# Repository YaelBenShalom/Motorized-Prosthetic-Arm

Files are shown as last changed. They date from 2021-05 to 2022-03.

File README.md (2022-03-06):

# The Design and Control of a Motorized Prosthetic Arm

Author: Yael Ben Shalom<br>
Final project, MS in Robotics at Northwestern, 2021.

## Table of Contents

- [Project Description](#project-description)
- [Project Overview](#project-overview)
- [Getting Started](#getting-started)

## Project Description

In this project, I designed, built, and controlled a motorized prosthetic elbow that imitates healthy arm motion to help amputees prevent falling, avoid injuries, and maintain balance while walking. According to [Kent and Major's research](https://www.sciencedirect.com/science/article/abs/pii/S0268003320301248?casa_token=pASJip1O0HgAAAAA:ckojZ8F55NSTF2rAq7aVUub568BDZgnYYnto9notnVSgfjbTsNp5ktE2Q-ZMWgL62Lgc80yd), asymmetries in body mass and motion affect the regulation of whole-body angular momentum in individuals with upper limb absence and may increase fall risk.

To better predict the arm-body motion, I analyzed arm movement data patterns, simulated full arm dynamics, and found the relation between walking speed to the angular velocity of the arm.

Please visit [my website](https://yaelbenshalom.github.io/motorized_prosthetic_arm/index.html) for more information about this project.

## Project Overview

This project contains 4 parts:

1. [Data collection](https://github.com/YaelBenShalom/Motorized-Prosthetic-Arm/tree/master/data)
2. [Arm motion analysis and modeling](https://github.com/YaelBenShalom/Motorized-Prosthetic-Arm/tree/master/motor_control/arm_pendulum_modeling)
3. [Motor control to achieve the desired arm motion](https://github.com/YaelBenShalom/Motorized-Prosthetic-Arm/tree/master/motor_control)
4. [Mechanical design of the prosthetic elbow](https://github.com/YaelBenShalom/Motorized-Prosthetic-Arm/tree/master/mech_design)

## Getting Started

1. Clone the repository:
    ```
    git clone https://github.com/YaelBenShalom/Motorized-Prosthetic-Arm.git
    ```

2. Install the `odrive-tool` package. For installation instructions, visit the [ODrive getting-started page](https://docs.odriverobotics.com/).

3. Assemble the system according to the system sketch.

4. Connect the module to the computer's USB port and upload the desired ODrive configuration by running:
    ```
    python3 setup.py
    ```

    The controller might need an additional tunning. Follow the tunning instructions on the [ODrive control page](https://docs.odriverobotics.com/control).

5. Activate the system by running:
    ```
    python3 motor_control/odrive_control.py --velocity=<walking velocity>
    ```

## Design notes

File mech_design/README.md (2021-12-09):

# The Design and Control of a Motorized Prosthetic Arm

Author: Yael Ben Shalom<br>
Final project, MS in Robotics at Northwestern, 2021.

## Mechanical Design of the Prosthetic Elbow

The system contained several key parts:

1. Motor (T-Motor, R60 KV115)
2. Encoder PCB (Designed for a Magnetic Rotary Encoder (AS5048A))
3. Driver (ODrive V3.6, 24V)
4. Odrive Adaptor PCB (Adaptor from ODrive connector to ethernet connector)
5. Elbow packaging (based on [Fillauer E-400](https://www.spsco.com/hosmer-e-400.html))
6. Battery

<p align="center">
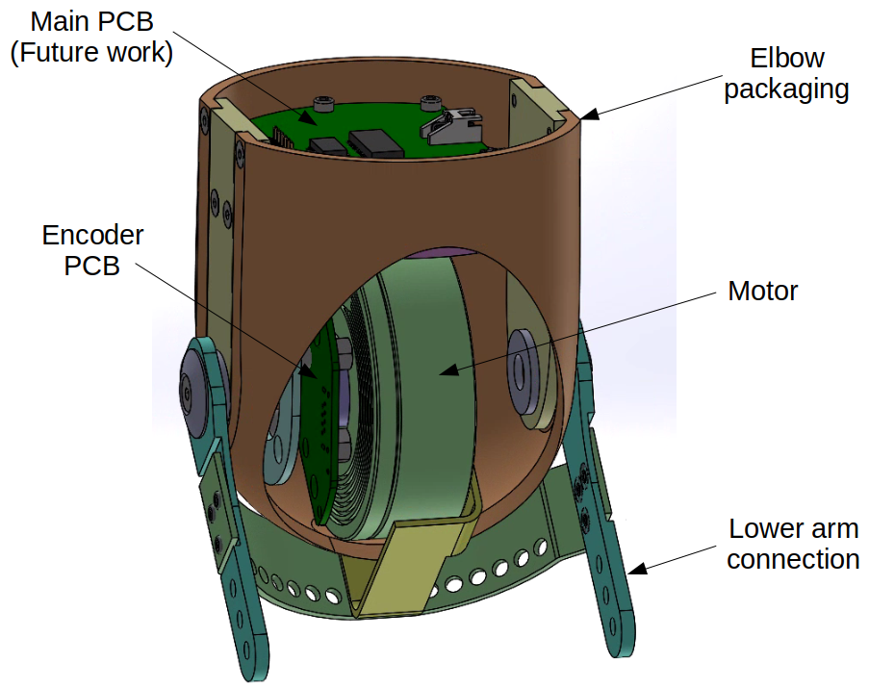
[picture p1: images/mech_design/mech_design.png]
  
</p>

All 3D CAD files can be found [here](https://github.com/YaelBenShalom/Motorized-Prosthetic-Arm/tree/master/mech_design), and all circuit board schematics and manufacture files can be found [here](https://github.com/YaelBenShalom/Motorized-Prosthetic-Arm/tree/master/board_design).

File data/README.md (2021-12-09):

# The Design and Control of a Motorized Prosthetic Arm

Author: Yael Ben Shalom<br>
Final project, MS in Robotics at Northwestern, 2021.

## Data Collection

In this part of the project, I focused on measuring prosthetics characteristics and collecting body-arm motion data.<br>
For further information about data collection please visit [my website](https://yaelbenshalom.github.io/motorized_prosthetic_arm/index.html).

This section contains all the data collected in this project and the scripts used to process it. It contains 2 main parts:
1. Prosthetic Measurements (length, mass, and center of mass location) to define the average prosthetic the device should support.
2. Walking data was collected from people with and without upper limb absence (including myself). The data was collected using sensors attached to the body in various locations (forearm, upper arm, lower back, etc.), that measured the body's angles, velocities, and accelerations. these were later used to explore the body-arm dynamics while walking, and to find the correlation between walking speed and arm swing

An example of the outputs of the sensors are presented in the following video:

<p align="center">
  
</p>

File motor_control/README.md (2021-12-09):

# The Design and Control of a Motorized Prosthetic Arm

Author: Yael Ben Shalom<br>
Final project, MS in Robotics at Northwestern, 2021.

## Motor Control to Achieve the Desired Arm Motion

To control the motor, I used a 2 layer control system - feedback current and position control. The current was controlled by the ODrive's controller, and the position was controlled by a feedback PID controller (with an optional feedforward component).

The control system diagram:

<p align="center">
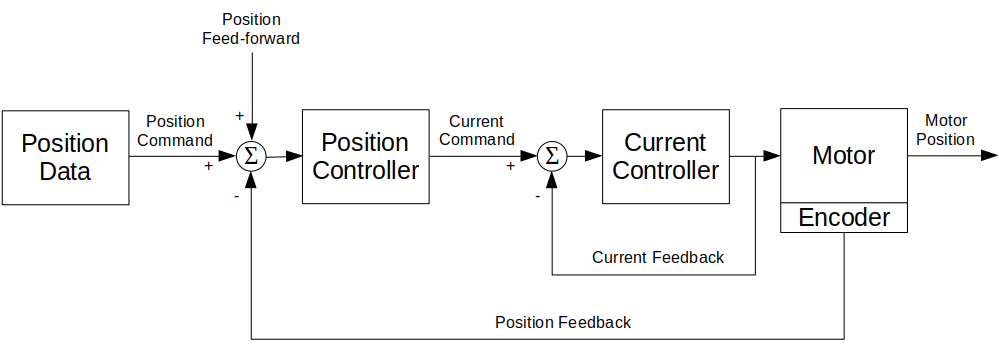
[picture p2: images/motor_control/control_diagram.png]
  
</p>

The PID position control diagram:

<p align="center">
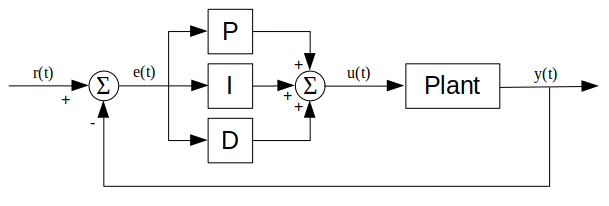
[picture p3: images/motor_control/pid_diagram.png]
  
</p>

An example of motor position control using the PID controller. The blue plot is the input angles, the red plot is the controlled output angles, and the second graph is the error changing with time:

<p align="center">
  
</p>

<p align="center">
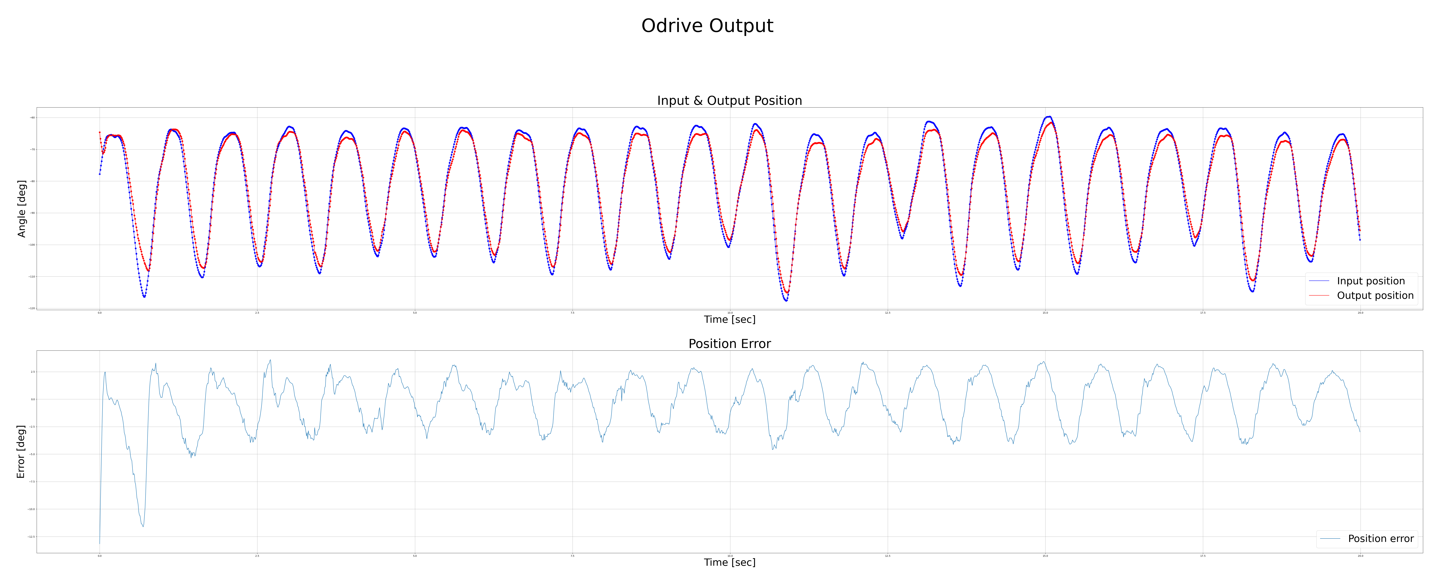
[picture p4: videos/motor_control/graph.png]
  
</p>

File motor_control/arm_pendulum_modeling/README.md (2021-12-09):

# The Design and Control of a Motorized Prosthetic Arm

Author: Yael Ben Shalom<br>
Final project, MS in Robotics at Northwestern, 2021.

## Arm Motion Analysis and Modeling

To Better understand the motion of a human arm and find a suitable motor to imitate the elbow motion, I modeled the arm as a double pendulum system. I used the system Lagrangian and measured shoulder and elbow angles to find the motion equations and extract the required elbow torque. More explanations about the theoretical aspects of the method and calculations can be found [here](https://yaelbenshalom.github.io/motorized_prosthetic_arm/index.html).

The double pendulum can be described using the following system sketch, where the masses are located in the center of mass of every link:

<p align="center">
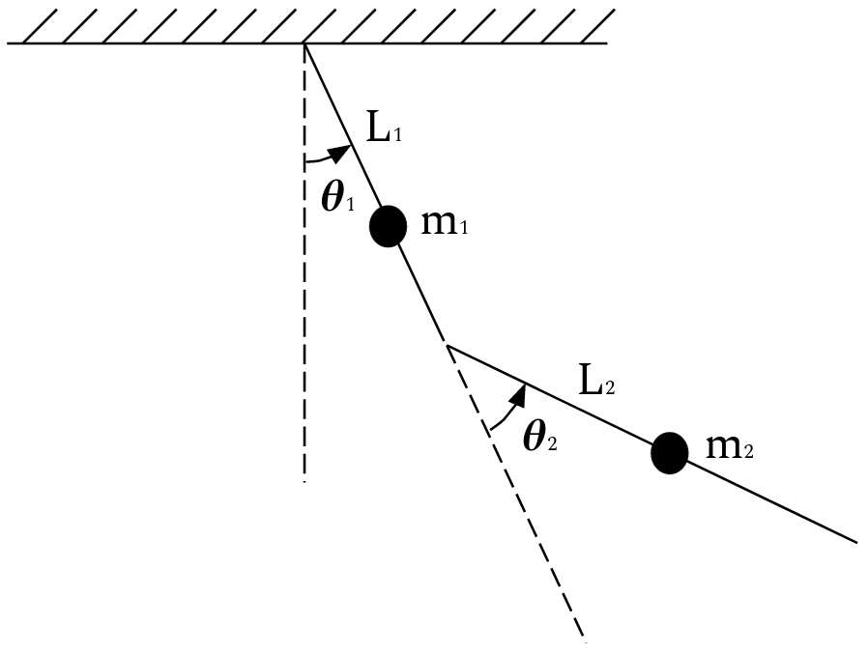
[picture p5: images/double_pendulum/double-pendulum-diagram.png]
  
</p>

The following video shows an animation of the arm motion, represented as a double pendulum:

<p align="center">
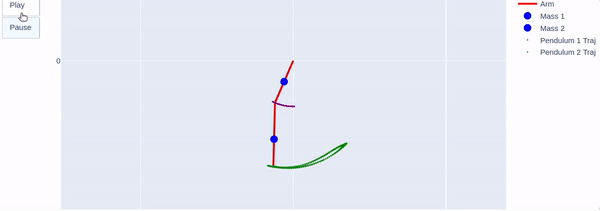
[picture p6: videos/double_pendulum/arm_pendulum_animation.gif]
  
</p>

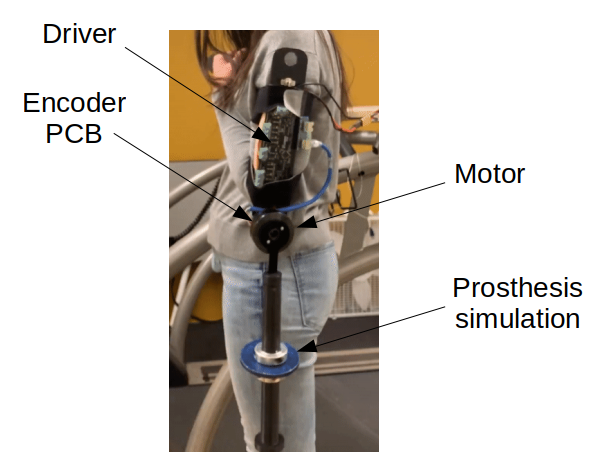
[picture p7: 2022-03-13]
images/mech_design/Prototype.png

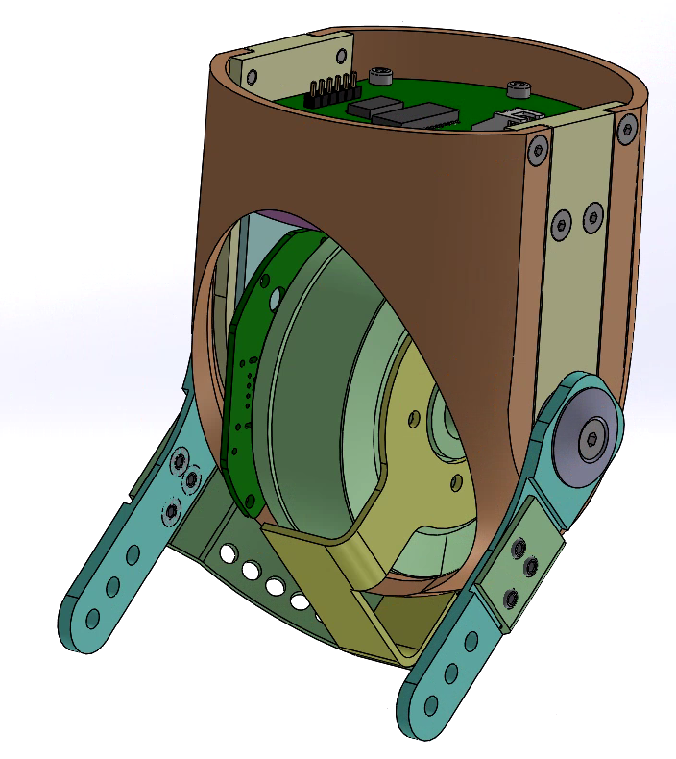
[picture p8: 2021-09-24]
images/mech_design/mech_design3.png

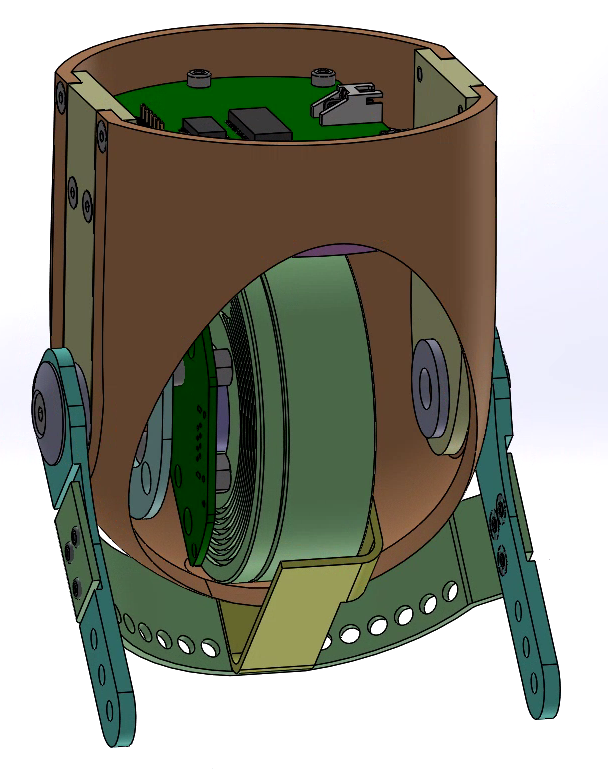
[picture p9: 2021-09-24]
images/mech_design/mech_design2.png

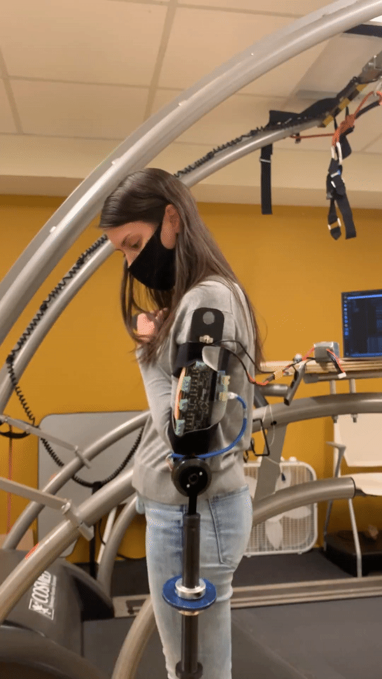
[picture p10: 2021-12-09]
images/mech_design/prototype2.png

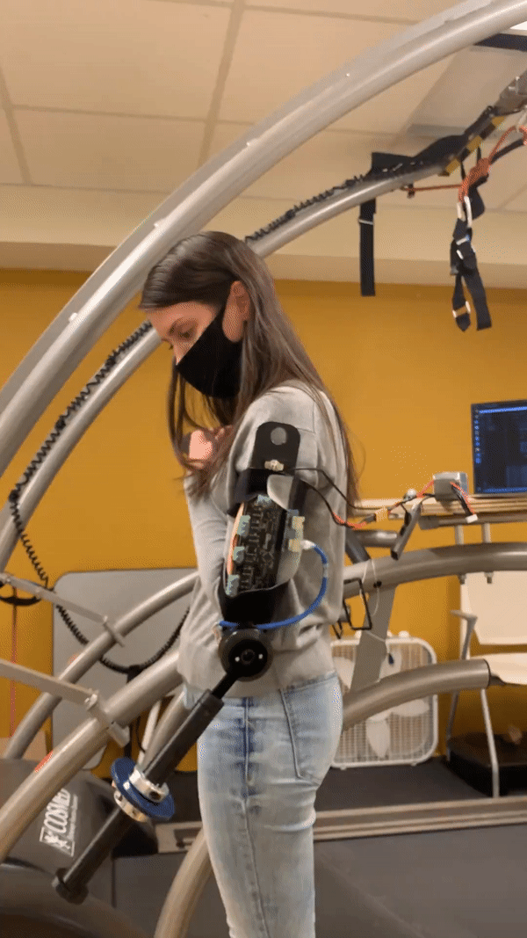
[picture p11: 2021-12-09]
images/mech_design/prototype1.png

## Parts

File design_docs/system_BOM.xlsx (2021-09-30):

Module | Component | Quantity | Purpose | Source
PCB | MPLAB Snap | 1 | Program the PIC | https://www.digikey.com/en/products/detail/PG164100/PG164100-ND/9562532?itemSeq=359206540
 | PIC32MX170F256B-50I/SP | 1 | PIC32 microcontroller - bread board | https://www.digikey.com/en/products/detail/microchip-technology/PIC32MX170F256B-50I-SS/4902613
 | PIC32MX170F256B-50I/SO | 1 | PIC32 microcontroller - PCB | https://www.digikey.com/en/products/detail/microchip-technology/PIC32MX170F256B-50I-SO/4902611
 | micro USB cable | 3 | power, programming and communication | https://www.digikey.com/en/products/detail/3025010-03/Q853-ND/4341883?itemSeq=359206541
 | 8 MHz resonator | 1 | PIC clock source | https://www.digikey.com/en/products/detail/CSTLS8M00G53-B0/490-1212-ND/584420?itemSeq=359206536
 | Pushbutton | 3 | Reset and User buttons | https://www.digikey.com/en/products/detail/EVQ-11A07K/P8072SCT-ND/259557?itemSeq=359206539
 | Green LED | 3 | indication | https://www.digikey.com/en/products/detail/WP132XGD/754-1210-ND/1747609?itemSeq=359206537
 | Red LED | 3 | indication | https://www.digikey.com/en/products/detail/WP132XID/754-1211-ND/1747610?itemSeq=359206531
 | Yellow LED | 3 | indication | https://www.digikey.com/en/products/detail/WP132XYD/754-1212-ND/1747611?itemSeq=359206534
 | 0.1uF capacitor | 5 | bypass | https://www.digikey.com/en/products/detail/K104Z15Y5VE5TL2/BC1148TR-ND/286602
 | 10uF tantalum capacitor | 1 | prototyping
 | 330 ohm resistor | 10 | LED current limit | https://www.digikey.com/en/products/detail/CF14JT330R/CF14JT330RTR-ND/1741399
 | 10k ohm resistor | 10 | pull-up | https://www.digikey.com/en/products/detail/CF14JT10K0/CF14JT10K0TR-ND/1741265
 | Slide switch | 1 | power on/off | https://www.adafruit.com/product/805
 | 6 DOF IMU | 1 | motion sensing | https://www.adafruit.com/product/4480
 | CP2104 Friend | 1 | USB to UART | https://www.adafruit.com/product/3309
 | micro USB connector breakout | 1 | breadboard power | https://www.pololu.com/product/2586
 | DRV8835 breakout board | 1 | dual H-bridge | https://www.pololu.com/product/2135
 | 3.3V step up / step down | 1 | voltage regulator | https://www.pololu.com/product/2122
 | Extra long header pins | 6+3 | prototyping | https://www.aliexpress.com/item/32651418137.html?spm=a2g0s.9042311.0.0.50904c4dIFFWhE
 | micro USB connector | 1 | PCB | https://www.digikey.com/en/products/detail/amphenol-icc-fci/10118194-0001LF/2785389
 | 28 position socket | 1 | PCB | https://www.digikey.com/en/products/detail/on-shore-technology-inc/ED281DT/4147600
Motor | R60 KV115 | 1 | Motor | https://store.tmotor.com/goods.php?id=943
Encoder | AS5048A-HTSP-500 | 1 | Encoder | https://www.digikey.com/en/products/detail/ams/AS5048A-HTSP-500/3188615
Driver | ODRIVE V3.6 | 1 | Driver | https://odriverobotics.com/shop/odrive-v36
Battery
Prototype | Breadboard | 3 | prototyping | https://www.circuitspecialists.com/solderless-breadboard-wb-102.html
 | Wire | 6 | prototyping | https://www.amazon.com/Tnisesm-Breadboard-Tweezers-Prototyping-Circuits/dp/B096K4SYTX
 | Bettomshin 2Pcs AXK0619 Thrust Needle Roller Bearings 0.24" x 0.75" x 0.16" High Carbon Chromium Bearing Steel Thrust Rolling Bearings with Washers | 2 | thrust bearing | https://www.amazon.com/dp/B08Z47TLR3 (https://www.amazon.com/dp/B08Z47TLR3?spLa=ZW5jcnlwdGVkUXVhbGlmaWVyP)
 | Bettomshin 2Pcs AXK0821 Thrust Needle Roller Bearings 0.31" x 0.83" x 0.08" High Carbon Chromium Bearing Steel Thrust Rolling Bearings with Washers | 2 | thrust bearing | https://www.amazon.com/dp/B08Z47FC6W (https://www.amazon.com/dp/B08Z47FC6W?spLa=ZW5jcnlwdGVkUXVhbGlmaWVyP)
 | 32 Mbit flash | 1 | memory for audio project | https://www.digikey.com/en/products/detail/W25Q32JVDAIQ/W25Q32JVDAIQ-ND/5803977?itemSeq=359206549
 | MCP23017 | 1 | I2C IO expander | https://www.digikey.com/en/products/detail/MCP23017-E%2fSP/MCP23017-E%2fSP-ND/894272?itemSeq=359206544
 | MCP4912 | 1 | SPI DAC | https://www.digikey.com/en/products/detail/MCP4912-E%2fP/MCP4912-E%2fP-ND/2332828?itemSeq=359206545
 | WS2812B | 5 | Addressable RGB LED (Neopixel) | https://www.digikey.com/en/products/detail/COM-12877/1568-1202-ND/5673788?itemSeq=359206543
 | L4931 3.3V regulator | 1

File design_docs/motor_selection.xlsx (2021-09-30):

 |  | Format legend: | Row checked by Bill | inferred/calculated spec |  | vendor spec | ~ = unknown | guess based on similar product
 |  |  |  |  |  |  |  |  |  |  |  |  |  |  |  |  |  |  |  |  |  |  | Normalized (1-normal for undesirable)
Vendor | Name | Rated Voltage (V) | Rated Current (A) | Peak Current (A) | Power (W) | Stall Current (A) | Rwinding (Ω) | Rated τ (Nm) | Peak τ (Nm) | Stall τ (Nm) | Rated ω (rpm) | Free ω (rpm) | Kv (rpm/V) | Reduction | MOI (g*cm²) | Pole Pairs | Mass (g) | Price | Stall τ to weight (Nm/kg) | Stall loss (W) | Effective Km | Notes | Stall τ to weight (Nm/kg) | Stall loss (W) | Effective Km | Average normal metric |  | Stall Diff (A) | Stall Diff Power (W)
T-Motor | G35 (https://uav-en.tmotor.com/html/2021/G_0106/653.html) | 16 | 1.45 | 4.5 | 23.2 | 4.5 | 3.33 | 0.15 | 0.46 | 0.46 | 900 | 1500 | 100 | 1 | 61 | 7 | 159 | $54.99 | 2.893081761 | 72 | 0.05421151989 |  | #DIV/0! | 0.99265625 | 0.03901156848 | #DIV/0! |  | 0.3048048048 | 4.876876877
T-Motor | AK80-6 (http://store-new.tmotor.com/goods.php?id=981) | 24 | 12 | 24 | 288 | 141.1764706 | 0.17 | 6 | 12 | 80.88815931 | 365 | 460 | 100 | 6 | ~ | 21 | 485 | $569.90 | 166.7797099 | 3388.235294 | 1.38962677 | Gearbox | #DIV/0! | 0.6544117647 | 1 |  | <-omitted from color scale | 0 | 0
T-Motor | G40 (https://uav-en.tmotor.com/html/2021/G_0106/652.html) | 16 | 1.65 | 5 | 26.4 | 5 | 3.6 | 0.25 | 0.73 | 0.73 | 600 | 1050 | 70 | 1 | 74 | 14 | 183 | $72.99 | 3.989071038 | 80 | 0.08161648118 |  | #DIV/0! | 0.9918402778 | 0.0587326633 | #DIV/0! |  | -0.5555555556 | -8.888888889
T-Motor | G60 (https://uav-en.tmotor.com/html/2021/G_0106/651.html) | 24 | 1.43 | 4.2 | 34.32 | 4.2 | 4.6 | 0.6 | 1.75 | 1.75 | 350 | 560 | 25 | 1 | 355 | 14 | 374 | $108.99 | 4.679144385 | 100.8 | 0.1743041722 |  | #DIV/0! | 0.98971875 | 0.125432365 | #DIV/0! |  | 1.017391304 | 24.4173913
ODrive | D5065 270KV (https://odriverobotics.com/shop/odrive-custom-motor-d5065) | 32 |  | 65 | 0 | 136.1702128 | 0.39 |  |  | 1.99 |  | 8640 | 270 | 1 | ~ | 7 | 420 | $70.00 | 4.738095238 | 4357.446809 | 0.03014650911
ODrive | D6374 150KV (https://odriverobotics.com/shop/odrive-custom-motor-d6374-150kv) | 48 |  | 70 | 0 | 204.2553191 | 0.39 |  |  | 3.86 |  | 5760 | 150 | 1 | ~ | 7 | 890 | $109.00 | 4.337078652 | 9804.255319 | 0.03898342552
Turnigy | 9225-90KV (https://hobbyking.com/en_us/9225-90kv-turnigy-multistar-brushless-multi-rotor-motor.html?queryID=27b34695562cad5fb798dcf916c7fe86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) | 48 | 0.5 | 36 | 24 | 204.2553191 | 0.186 |  |  | 3.307973373 |  | 3456 | 90 | 1 | ~ |  | 401 | $168.71 | 8.249310156 | 9804.255319 | 0.03340832476
Turnigy | 9235-100KV (https://hobbyking.com/en_us/9235-100kv-turnigy-multistar-brushless-multi-rotor-motor.html) | 48 | 1 | 57 | 48 | 204.2553191 | 0.055 |  |  | 4.713862056 |  | 3840 | 100 | 1 | ~ |  | 674 | $103.00 | 6.993860617 | 9804.255319 | 0.04760686279
Turnigy | 5035-125KV (https://hobbyking.com/en_us/dt6376-14p-sensored-motor-125kv.html?queryID=85e71f1db46e4db3044ad070fd4c15bf&objectID=63717&indexName=hbk_live_products_analytics) | 48 | 0.9 | 45 | 43.2 | 204.2553191 | 0.09 |  |  | 2.977176035 |  | 4800 | 125 | 1 | ~ |  | 745 | $119.99 | 3.996209443 | 9804.255319 | 0.03006749229
Turnigy | 6354-140KV (https://hobbyking.com/en_us/turnigy-sk8-6354-140kv-sensored-brushless-motor-14p.html?queryID=f6b3d9bf906308e4f94016e6499b63a8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) | 48 | 0.7 | 42 | 33.6 | 204.2553191 | 0.098 |  |  | 2.480980029 |  | 5376 | 140 | 1 | ~ |  | 630 | $99.99 | 3.938063539 | 9804.255319 | 0.02505624357
Turnigy | 6374-149KV (https://hobbyking.com/en_us/turnigy-sk8-6374-149kv-sensored-brushless-motor-14p.html?queryID=28a215a988cff0201e40fbcf5f789194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) | 48 | 1.3 | 80 | 62.4 | 204.2553191 | 0.043 |  |  | 4.440232715 |  | 5721.6 | 149 | 1 | ~ |  | 937 | $119.99 | 4.738775576 | 9804.255319 | 0.04484338895
Turnigy | 6374-192KV (https://hobbyking.com/en_us/turnigy-sk8-6374-192kv-sensored-brushless-motor-14p.html?queryID=fee355d7e01e4a0f2609152654ff0b63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) | 48 | 1.8 | 100 | 86.4 | 204.2553191 | 0.024 |  |  | 4.307256995 |  | 7372.8 | 192 | 1 | ~ |  | 940 | $199.99 | 4.582188293 | 9804.255319 | 0.04350042287
Turnigy | RotoMax-231KV (https://hobbyking.com/en_us/turnigy-rotomax-1-60-brushless-outrunner-motor.html?queryID=f6b3d9bf906308e4f94016e6499b63a8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) | 48 | 1.47 | 80 | 70.56 | 204.2553191 | 0.028 |  |  | 2.86404621 |  | 8870.4 | 231 | 1 | ~ | 24 | 849 | $166.99 | 3.373434876 | 9804.255319 | 0.02892495651
Turnigy | 5060 270KV (https://hobbyking.com/en_us/propdrive-v2-5060-270kv-brushless-outrunner-motor.html?queryID=fee355d7e01e4a0f2609152654ff0b63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) | 32 |  | 90 | 0 | 136.1702128 | 0.036 |  |  | 2.756644477 |  | 8640 | 270 | 1 | ~ |  | 438 | $66.99 | 6.293708852 | 4357.446809 | 0.04176040596
Turnigy | G90-325KV (https://hobbyking.com/en_us/turnigy-g90-325kv-brushless-outrunner-motor-90-glow.html?queryID=fee355d7e01e4a0f2609152654ff0b63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) | 24 | 2 | 52 | 48 | 102.1276596 | 0.036 |  |  | 1.323189349 |  | 7800 | 325 | 1 | ~ |  | 600 | $69.99 | 2.205315582 | 2451.06383 | 0.02672665981
T-Motor | GL100 (KV10) (https://store-en.tmotor.com/goods.php?id=1128) | 24 | 2.8 | 8.4 | 67.2 | 8.4 | 2.6 | 3 | 7.8 | 7.7 | 140 | 240 | 10 | 1 | ~ | ~ | 698 | $272.99 | 11.03151862 | 201.6 | 0.5423073135 |  | #DIV/0! | 0.9794375 | 0.3902539339 | #DIV/0! |  | 0.8307692308 | 19.93846154
T-Motor | GL80 (KV30) (https://uav-en.tmotor.com/html/2021/GLSeries_0225/709.html) | 24 | 1.43 | 4.2 | 34.32 | 4.2 | 4.6 | 0.6 | 1.75 | 1.75 | 350 | 720 | 30 | 1 | ~ | 21 | 315 | $181.99 | 5.555555556 | 100.8 | 0.1743041722 |  | #DIV/0! | 0.98971875 | 0.125432365 | #DIV/0! |  | 1.017391304 | 24.4173913
T-Motor | GL80 (KV60) (https://uav-en.tmotor.com/html/2021/GLSeries_0225/709.html) | 24 | 5.8 | 17 | 139.2 | 17 | 0.41 | 1 | 2.9 | 2.9 | 1050 | 1440 | 60 | 1 | ~ | 21 | 315 | $181.99 | 9.206349206 | 408 | 0.1435713937 |  | #DIV/0! | 0.9583854167 | 0.1033165141 | #DIV/0! |  | 41.53658537 | 996.8780488
T-Motor | GL60 (KV25) (https://uav-en.tmotor.com/html/2021/GLSeries_0225/708.html) | 24 | 1.43 | 4.2 | 34.32 | 4.2 | 4.6 | 0.6 | 1.75 | 1.75 | 350 | 600 | 25 | 1 | ~ | 14 | 230 | $108.99 | 7.608695652 | 100.8 | 0.1743041722 |  | #DIV/0! | 0.98971875 | 0.125432365 | #DIV/0! |  | 1.017391304 | 24.4173913
T-Motor | GL60 (KV55) (https://uav-en.tmotor.com/html/2021/GLSeries_0225/708.html) | 24 | 3.1 | 9.5 | 74.4 | 9.5 | 1.1 | 0.6 | 1.75 | 1.75 | 850 | 1200 | 50 | 1 | ~ | 14 | 226 | $108.99 | 7.743362832 | 228 | 0.1158965812 |  | #DIV/0! | 0.9767447917 | 0.08340122958 | #DIV/0! |  | 12.31818182 | 295.6363636
T-Motor | GL40 (https://uav-en.tmotor.com/html/2021/GLSeries_0225/707.html) | 16 | 1.65 | 5 | 26.4 | 5 | 3.6 | 0.25 | 0.73 | 0.73 | 600 | 1120 | 70 | 1 | ~ | 14 | 107 | $72.99 | 6.822429907 | 80 | 0.08161648118 |  | #DIV/0! | 0.9918402778 | 0.0587326633 | #DIV/0! |  | -0.5555555556 | -8.888888889
T-Motor | GL35 (https://uav-en.tmotor.com/html/2021/GLSeries_0225/706.html) | 16 | 1.45 | 4.5 | 23.2 | 4.5 | 3.33 | 0.15 | 0.46 | 0.46 | 900 | 1600 | 100 | 1 | ~ | 7 | 90 | $54.99 | 5.111111111 | 72 | 0.05421151989 |  | #DIV/0! | 0.99265625 | 0.03901156848 | #DIV/0! |  | 0.3048048048 | 4.876876877
T-Motor | GB36-1 (https://uav-en.tmotor.com/html/2018/GB_0330/19.html) | 25.2 | ~ | 1.615384615 | #VALUE! | 1.615384615 | 15.6 | 0.1028385786 | 0.3085157358 | 0.3085157358 | ~ | 1260 | 50 | 1 | ~ | 7 | 88 | $49.90 | 3.505860635 | 40.70769231 | 0.0483547429 |  | #DIV/0! | 0.9958479567 | 0.03479692818 | #DIV/0! |  | 0 | 0
T-Motor | GB54-1 (https://store-en.tmotor.com/goods.php?id=444) | 25.2 | ~ | 1.984251969 | #VALUE! | 1.984251969 | 12.7 | 0.1913960661 | 0.5741881984 | 0.5741881984 | ~ | 831.6 | 33 | 1 | ~ | 7 | 137 | $69.90 | 4.191154733 | 50.00314961 | 0.08119991632 |  | #DIV/0! | 0.9948998524 | 0.05843289586 | #DIV/0! |  | 0 | 0
T-Motor | GB54-2 (https://store-en.tmotor.com/goods.php?id=445) | 25.2 | ~ | 1.68 | #VALUE! | 1.68 | 15 | 0.2056771572 | 0.6170314717 | 0.6170314717 | ~ | 655.2 | 26 | 1 | ~ | 7 | 156 | $74.90 | 3.955329947 | 42.336 | 0.09483145293 |  | #DIV/0! | 0.995681875 | 0.0682423907 | #DIV/0! |  | 0 | 0
T-Motor | GB4106 (https://store-en.tmotor.com/goods.php?id=443) | 25.2 | ~ | 1.647058824 | #VALUE! | 1.647058824 | 15.3 | 0.09891983144 | 0.2967594943 | 0.2967594943 | ~ | 1335.6 | 53 | 1 | ~ | 7 | 70 | $45.90 | 4.239421348 | 41.50588235 | 0.04606274308 |  | #DIV/0! | 0.9957665441 | 0.03314756457 | #DIV/0! |  | 0 | 0
T-Motor | R60 (https://store-en.tmotor.com/goods.php?id=943) | 48 | 9 | 28 | 432 | 204.2553191 | 0.235 | 0.75 | 2.3 | 16.9608228 | 4150 | 5520 | 115 | 1 | ~ | 14 | 248 | $177.90 | 68.39041451 | 9804.255319 | 0.171292998 |  | #DIV/0! | 0 | 0.1232654708 | #DIV/0! |  | 0 | 0
T-Motor | R80 (https://store-en.tmotor.com/goods.php?id=944) | 48 | 15 | 46 | 720 | 204.2553191 | 0.235 | 1.3 | 4 | 17.73176929 | 4600 | 5280 | 110 | 1 | ~ | 21 | 354 | $258.90 | 50.08974375 | 9804.255319 | 0.1790790434 |  | #DIV/0! | 0 | 0.1288684468 | #DIV/0! |  | 0 | 0
T-Motor | RI50 (https://store-en.tmotor.com/goods.php?id=856) | 48 | 5.3 | 15.25 | 254.4 | 33.8028169 | 1.42 | 0.58 | 1.67 | 3.362428375 | 3020 | 4608 | 96 | 1 | 22.81 | 7 | 180.8 | $61.90 | 18.59750208 | 1622.535211 | 0.08347491333 | Frameless | #DIV/0! | 0.8345070423 | 0.06007002395 |  | <-omitted from color scale | 0 | 0
T-Motor | RI60 (https://store-en.tmotor.com/goods.php?id=857) | 48 | 6.7 | 19.2 | 321.6 | 53.33333333 | 0.9 | 0.57 | 1.63 | 4.107224338 | 3495 | 5952 | 124 | 1 | 33.05 | 14 | 155.9 | $98.90 | 26.34524912 | 2560 | 0.08117614856 | Frameless | #DIV/0! | 0.7388888889 | 0.05841579216 |  | <-omitted from color scale | 0 | 0
T-Motor | RI70 (https://store-en.tmotor.com/goods.php?id=858) | 48 | 8.4 | 24 | 403.2 | 114.8325359 | 0.418 | 0.94 | 2.68 | 11.5428415 | 3125 | 4560 | 95 | 1 | 92.15 | 14 | 270.4 | $123.90 | 42.68802331 | 5511.961722 | 0.1554746672 | Frameless | #DIV/0! | 0.4377990431 | 0.1118823202 |  | <-omitted from color scale | 0 | 0
T-Motor | RI80 (https://store-en.tmotor.com/goods.php?id=860) | 48 | 10.4 | 29.3 | 499.2 | 171.4285714 | 0.28 | 1.45 | 4.1 | 21.82696362 | 2805 | 3600 | 75 | 1 | 176.68 | 7 | 411.2 | $132.90 | 53.08113722 | 8228.571429 | 0.2406196568 | Frameless | #DIV/0! | 0.1607142857 | 0.1731541605 |  | <-omitted from color scale | 0 | 0
T-Motor | G100 (https://store-en.tmotor.com/goods.php?id=957) | 24 | 2.8 | 8.4 | 67.2 | 8.4 | 2.6 | 3 | 7.8 | 7.7 | 140 | 250 | 10 | 1 | 2310 | 20 | 954 | $272.99 | 8.071278826 | 201.6 | 0.5423073135 |  | #DIV/0! | 0.9794375 | 0.3902539339 | #DIV/0! |  | 0.8307692308 | 19.93846154
T-Motor | G80 (KV60) (https://store-en.tmotor.com/goods.php?id=956) | 24 | 5.8 | 13.8 | 139.2 | 17 | 0.41 | 1 | 4.5 | 2.9 | 1050 | 1400 | 60 | 1 | 650 | 21 | 482 | $181.99 | 6.01659751 | 408 | 0.1435713937 |  | #DIV/0! | 0.9583854167 | 0.1033165141 | #DIV/0! |  | 41.53658537 | 996.8780488
T-Motor | G80 (KV30) (https://store-en.tmotor.com/goods.php?id=956) | 24 | 2.8 | 55 | 67.2 | 8.3 | 1.64 | 1 | 8.6 | 2.9 | 450 | 700 | 30 | 1 | 650 | 21 | 472 | $181.99 | 6.144067797 | 199.2 | 0.205472323 |  | #DIV/0! | 0.9796822917 | 0.1478615175 | #DIV/0! |  | 6.334146341 | 152.0195122
T-Motor | AK60-6 (http://store-new.tmotor.com/goods.php?id=1138) | 24 | 7.4 | 22 | 177.6 | 91.60305344 | 0.262 | 3 | 9 | 37.48905966 | 400 | 560 | 140 | 6 | ~ | 14 | 315 | $298.90 | 119.0128878 | 2198.473282 | 0.7995469134 | Gearbox | #DIV/0! | 0.7757633588 | 0.5753680995 |  | <-omitted from color scale | 0 | 0
iPower | GBM5208H-200T (https://www.robotshop.com/en/ipower-gbm5208h-200t-gimbal-motor.html) | 22.2 | 0.066 | 10 | 1.4652 | 1.432258065 | 15.5 | 0.02498505242 | 0.5421976186 | 0.5421976186 | 560 | 560 | 25.22522523 | 1 | ~ | 7 | 203 | $49.99 | 2.670924229 | 31.79612903 | 0.09615469184 |  | #DIV/0! | 0.9967569052 | 0.06919461682 | #DIV/0! |  | 0 | 0
T-Motor | GL30 (https://store-en.tmotor.com/goods.php?id=1123) | 12 | 2.3 | 8.75 | 27.6 | 8.5 | 1.53 | 0.08 |  | 0.28 | 2200 | 3480 | 290 | 1 | ~ |  | 41 | $50.99 | 6.829268293 | 102 | 0.0277241312 |  | #DIV/0! | 0.9895963542 | 0.01995077514 | #DIV/0! |  | -0.6568627451 | -7.882352941
E-S Motor | 28PG-385SP-19-EN (https://www.robotshop.com/en/12v-28mm-planetary-gear-motor-with-encoder-306rpm.html) | 12 |  |  | 0 | 1.2 |  | 0.980665 | 3.726527 | 3.726527 | 306 | 310 | 25.83333333 | 19 | ~ | ~ |  | $18.95 | #DIV/0! | 14.4 | 0.9820260902 |  | #DIV/0! | 0.99853125 | 0.7066833424 | #DIV/0! |  | #DIV/0! | #DIV/0!
iPower | GBM4108H-120T (https://www.robotshop.com/en/ipower-gbm4108h-120t-gimbal-motor.html) | 20 | 1.5 | ~ | 30 | 1.801801802 | 11.1 | 0.2794916074 | 0.3357256545 | 0.3357256545 | 1025 | 1025 | 51.25 | 1 | ~ | 11 | 125 | $40.95 | 2.685805236 | 36.03603604 | 0.05592629162 |  | #DIV/0! | 0.9963244494 | 0.04024554855 | #DIV/0! |  | 0 | 0
Maxon | 614949 (https://www.maxongroup.us/maxon/view/product/motor/ecmotor/ecflat/ecflat60/614949?etcc_cu=onsite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) | 24 | 9.28 | 81.9 | 222.72 | 81.9 | 0.293 | 0.536 | 4.3 | 4.3 | 3240 | 4300 | 182 | 1 | 832 | 7 | 360 | $162.00 | 11.94444444 | 1965.6 | 0.09698864318 |  | #DIV/0! | 0.799515625 | 0.06979474295 | #DIV/0! |  | 0.01126279863 | 0.2703071672
Maxon | 591483 (https://www.maxongroup.us/maxon/view/product/motor/ecmotor/ecflat/ecflat45/591483) | 60 | 1.06 | 8.14 | 63.6 | 8.14 | 7.37 | 0.17 | 1.24 | 1.24 | 2890 | 3720 | 62.8 | 1 | 181 | 8 | 140 | $184.25 | 8.857142857 | 488.4 | 0.05610917169 |  | #DIV/0! | 0.9501848958 | 0.04037715228 | #DIV/0! |  | 0.001112618725 | 0.06675712347
Maxon | 608138 (https://www.maxongroup.us/maxon/view/product/motor/ecmotor/ecflat/ecflat45/608138) | 48 | 1.76 | 13.3 | 84.48 | 13.3 | 3.61 | 0.149 | 1.04 | 1.04 | 4300 | 5740 | 121 | 1 | 135 | 8 | 110 | $178.50 | 9.454545455 | 638.4 | 0.04116109315 |  | #DIV/0! | 0.9348854167 | 0.02962025059 | #DIV/0! |  | -0.003601108033 | -0.1728531856
T-Motor | G30 (https://store-en.tmotor.com/goods.php?id=952) | 12 | 2.3 | 8.75 | 27.6 | 8.5 | 1.53 | 0.08 | 0.3 | 0.28 | 2200 | 3480 | 290 | 1 | 24.2 | 7 | 83 | $50.99 | 3.373493976 | 102 | 0.0277241312 |  | #DIV/0! | 0.9895963542 | 0.01995077514 | #DIV/0! |  | -0.6568627451 | -7.882352941
Pololu | 131:1 Metal Gearmotor 37Dx73L mm 12V with 64 CPR Encoder (Helical Pinion) (https://www.pololu.com/product/2828/specs) | 12 | 5.5 |  | 66 | 5.5 |  | 0.63743225 | 4.4129925 | 4.4129925 | 66 | 76 | 6.333333333 | 131 | ~ | ~ | 210 | $39.95 | 21.01425 | 66 | 0.5432018265 |  | #DIV/0! | 0.9932682292 | 0.3908976413 | #DIV/0! |  | #DIV/0! | #DIV/0!
Pololu | 150:1 Metal Gearmotor 37Dx73L mm 12V with 64 CPR Encoder (Helical Pinion) (https://www.pololu.com/product/2828/specs) | 12 | 5.5 |  | 66 | 5.5 |  | 0.63743225 | 4.8052585 | 4.8052585 | 58 | 67 | 5.583333333 | 150 | ~ | ~ | 210 | $39.95 | 22.88218333 | 66 | 0.5914864333 |  | #DIV/0! | 0.9932682292 | 0.4256440983 | #DIV/0! |  | #DIV/0! | #DIV/0!
Pololu | 131:1 Metal Gearmotor 37Dx73L mm 24V with 64 CPR Encoder (Helical Pinion) (https://www.pololu.com/product/2828/specs) | 24 | 3 |  | 72 | 3 |  | 0.63743225 | 4.6091255 | 4.6091255 | 68 | 79 | 3.291666667 | 131 | ~ | ~ | 210 | $39.95 | 21.94821667 | 72 | 0.5431906494 |  | #DIV/0! | 0.99265625 | 0.390889598 | #DIV/0! |  | #DIV/0! | #DIV/0!
Pololu | 150:1 Metal Gearmotor 37Dx73L mm24V with 64 CPR Encoder (Helical Pinion) (https://www.pololu.com/product/2828/specs) | 24 | 3 |  | 72 | 3 |  | 0.63743225 | 5.491724 | 5.491724 | 59 | 68 | 2.833333333 | 150 | ~ | ~ | 210 | $39.95 | 26.15106667 | 72 | 0.6472058801 |  | #DIV/0! | 0.99265625 | 0.4657407977 | #DIV/0! |  | #DIV/0! | #DIV/0!
E-S Motor | 36GP-555PM-139-EN 24V (https://www.robotshop.com/en/36d-dc-planetary-gearmotor-w-encoder-24v-230rpm.html) | 24 | 2.7 |  | 64.8 | 1.2 |  | 3.4323275 | 4.903325 | 4.903325 | 65 | 85 | 3.541666667 | 51 | ~ | ~ |  | $36.50 | #DIV/0! | 28.8 | 0.913680668 |  | #DIV/0! | 0.9970625 | 0.6575007678 | #DIV/0! |  | #DIV/0! | #DIV/0!
E-S Motor | 36GP-555PM-100-EN 24V (https://www.robotshop.com/en/36d-dc-planetary-gearmotor-w-encoder-24v-230rpm.html) | 24 | 2.7 |  | 64.8 | 1.2 |  | 3.4323275 | 4.903325 | 4.903325 | 90 | 120 | 5 | 51 | ~ | ~ |  | $36.50 | #DIV/0! | 28.8 | 0.913680668 |  | #DIV/0! | 0.9970625 | 0.6575007678 | #DIV/0! |  | #DIV/0! | #DIV/0!
E-S Motor | 36GP-555PM-51-EN 24V (https://www.robotshop.com/en/36d-dc-planetary-gearmotor-w-encoder-24v-230rpm.html) | 24 | 2.7 |  | 64.8 | 1.2 |  | 3.4323275 | 4.903325 | 4.903325 | 190 | 230 | 9.583333333 | 51 | ~ | ~ |  | $36.50 | #DIV/0! | 28.8 | 0.913680668 |  | #DIV/0! | 0.9970625 | 0.6575007678 | #DIV/0! |  | #DIV/0! | #DIV/0!
Maxon | 608150 (https://www.maxongroup.us/maxon/view/product/motor/ecmotor/ecflat/ecflat45/608150) | 48 | 1.78 | 15.6 | 85.44 | 15.6 | 3.07 | 0.146 | 1.26 | 1.26 | 4510 | 5580 | 118 | 1 | 181 | 8 | 140 | $199.63 | 9 | 748.8 | 0.04604554601 |  | #DIV/0! | 0.923625 | 0.03313518926 | #DIV/0! |  | 0.03517915309 | 1.688599349
 |  |  |  |  | convert kv to Nm | 8.269933431

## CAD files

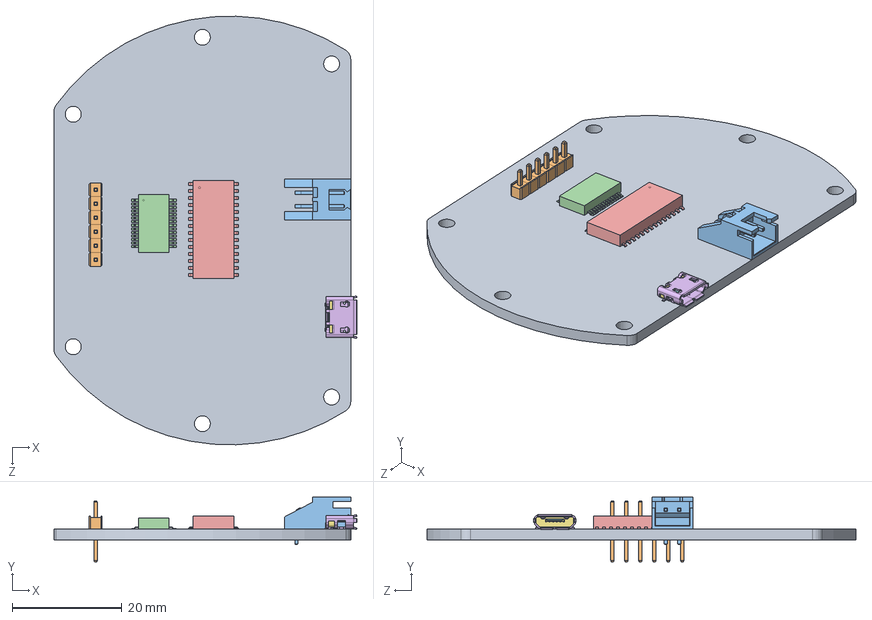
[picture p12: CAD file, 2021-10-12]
mech_design/CAD_model/PCB_assy.SLDASM
55.1 x 11.8 x 78.0 mm
PCB
1_Male_Pin_2.54_mm.STEP x 6
JST 2pin Right Receptacle
SSOP28_MC_MCH
SOIC28-W_MC_MCH
shield.stp
socket_housing.stp
socket_plate.stp
terminal.stp x 5

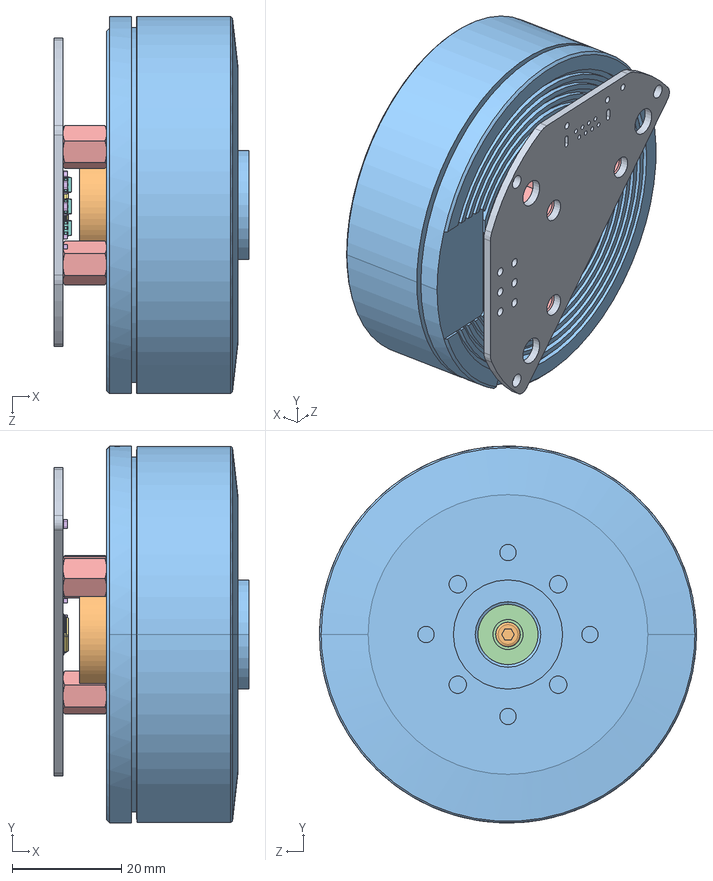
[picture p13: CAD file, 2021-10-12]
mech_design/CAD_model/motor_encoder_assy.SLDASM
35.6 x 69.0 x 69.0 mm
encoder-magnet
magnet-top-bracket
R60
magnet-bottom-bracket
hexagonal_spacer_MF_M4_H08_HEX7_FTD4_MTL8.step x 3
SOLID-0.step x 9
SOLID-1.step
SOLID-2.step x 3
COMPOUND.step
hex_socket_cylindrical_head_M2.5x12.step

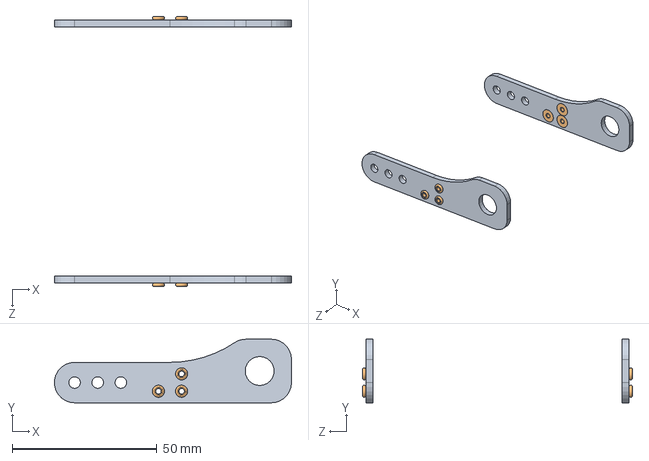
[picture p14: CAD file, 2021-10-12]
mech_design/CAD_model/joint_assy.SLDASM
81.9 x 22.0 x 93.4 mm
joint_lower x 2
rivet DIN 7337 x 6

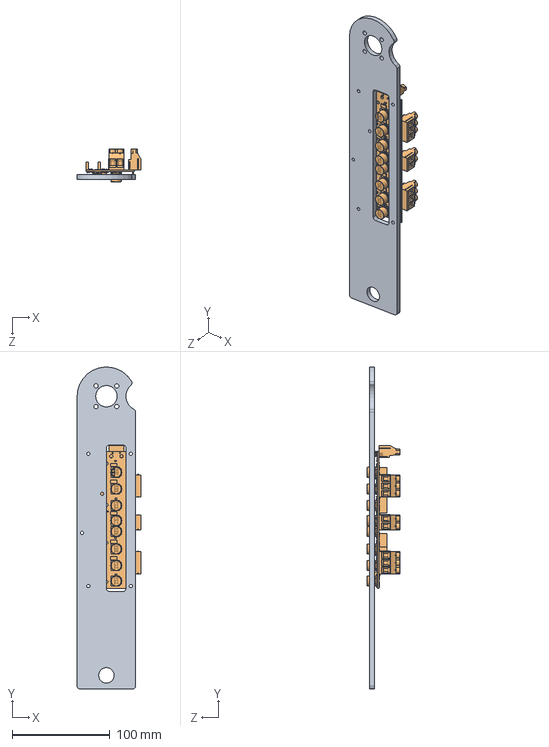
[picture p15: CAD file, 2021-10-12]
mech_design/CAD_model/stator_test_assy.SLDASM
65.3 x 330.0 x 33.7 mm
motor_bracket_stator_test
PCBasembly_simp

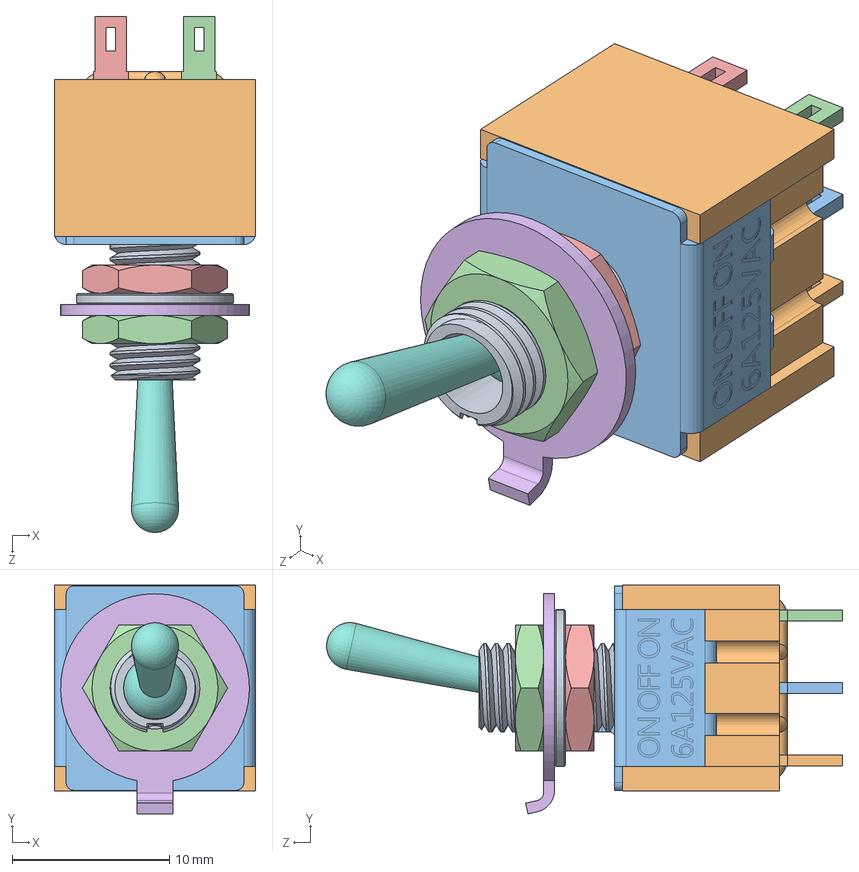
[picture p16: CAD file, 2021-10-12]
mech_design/CAD_model/ToggleSwitch 6Pin.stp.SLDASM
12.8 x 14.6 x 32.8 mm
Washer.stp
PIN_1of6.stp
PIN_2of6.stp
PIN_3of6.stp
PIN_4of6.stp
PIN_5of6.stp
PIN_6of6.stp
Batton Clone 1.stp
Thread.stp
Plastic Body.stp
Sheetmatal Frame.stp
Nut M6x0.75mm clone.stp
Nut M6x0.75mm.stp
Washer Anti Twist Protection.stp

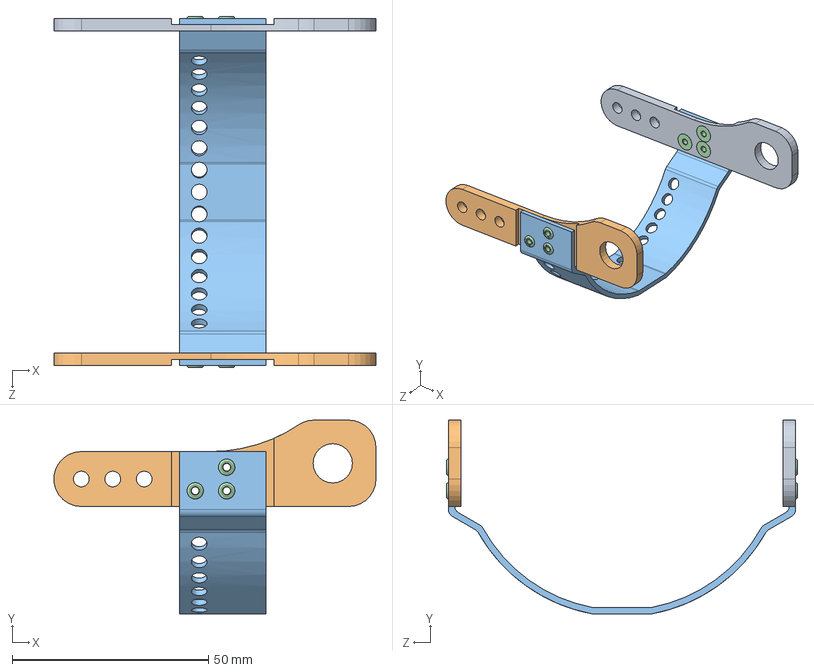
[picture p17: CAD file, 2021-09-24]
mech_design/CAD_model/joint_lower_assy3.SLDASM
81.9 x 49.3 x 89.4 mm
joint_lower_right
joint_lower_left
joint_lower_bridge3
Заклепка головка потайная DIN 7337 B x 6

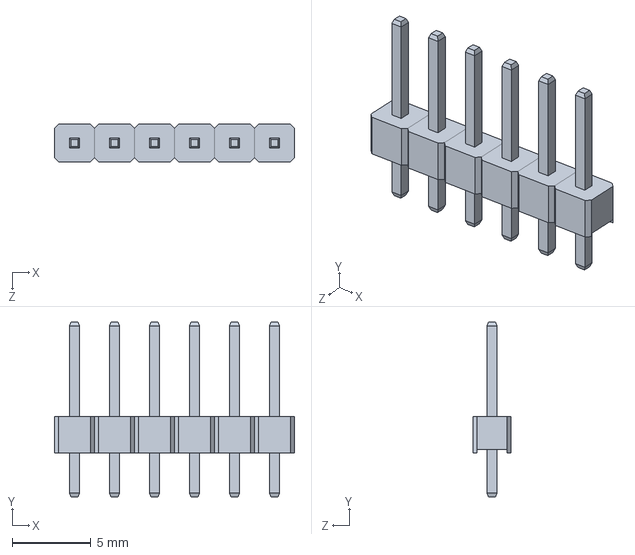
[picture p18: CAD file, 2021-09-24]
mech_design/CAD_model/6x_Male_Pin_2.54_mm.STEP.SLDASM
15.2 x 11.1 x 2.40 mm
1_Male_Pin_2.54_mm.STEP x 6

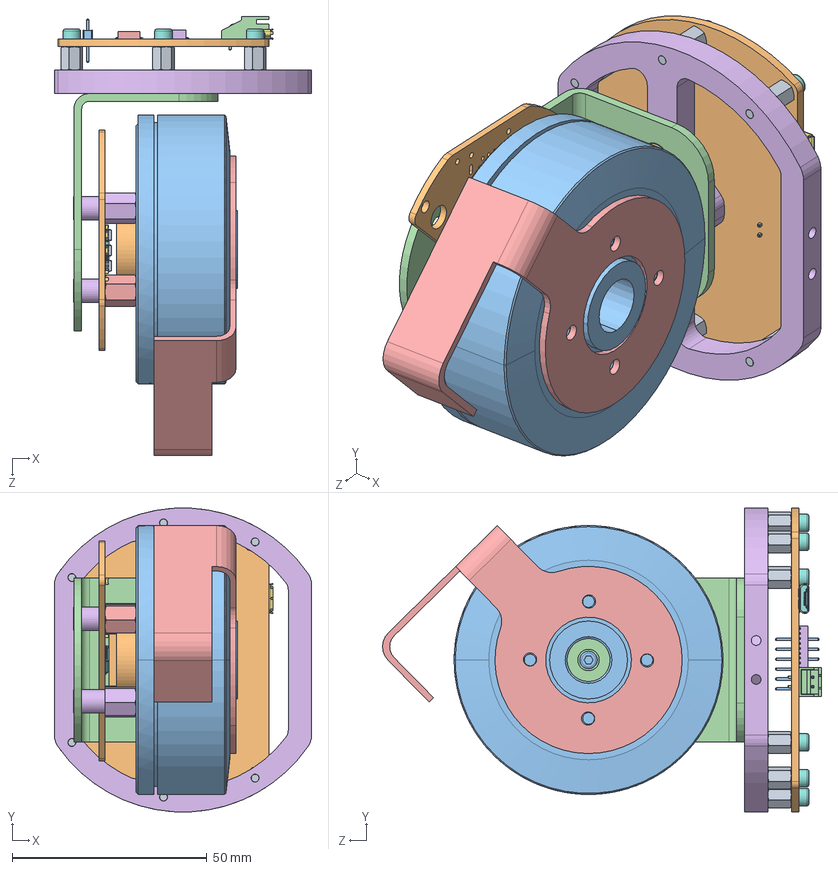
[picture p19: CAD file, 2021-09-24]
mech_design/CAD_model/mechatronics_assy.SLDASM
66.0 x 78.0 x 112.6 mm
encoder-magnet
magnet-top-bracket
R60
magnet-bottom-bracket
hexagonal_spacer_MF_M4_H08_HEX7_FTD4_MTL8.step
hexagonal_spacer_MF_M4_H14_HEX7_FTD8_MTL8_machined x 3
SOLID-0.step x 9
SOLID-1.step
SOLID-2.step x 3
COMPOUND.step
hex_socket_cylindrical_head_M2.5x12.step
motor_bracket_stator
motor_bracket_rotor
upper_plate
hex_socket_button_head_M3x06.step x 6
hex_socket_cylindrical_head_M2.5x06 x 6
hexagonal_spacer_MF_M2.5_H06_HEX5_FTD3_MTL6.step x 6
PCB
1_Male_Pin_2.54_mm.STEP x 6
JST 2pin Right Receptacle.step
SSOP28_MC_MCH
SOIC28-W_MC_MCH
shield.stp
socket_housing.stp
socket_plate.stp
terminal.stp x 5

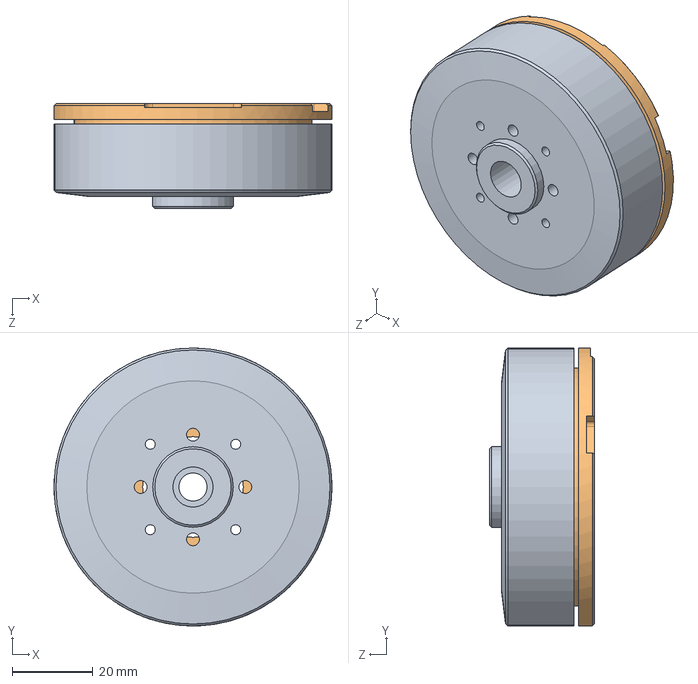
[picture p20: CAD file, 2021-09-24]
mech_design/CAD_model/motor.SLDASM
69.0 x 69.0 x 26.0 mm
motor_front
motor_rear

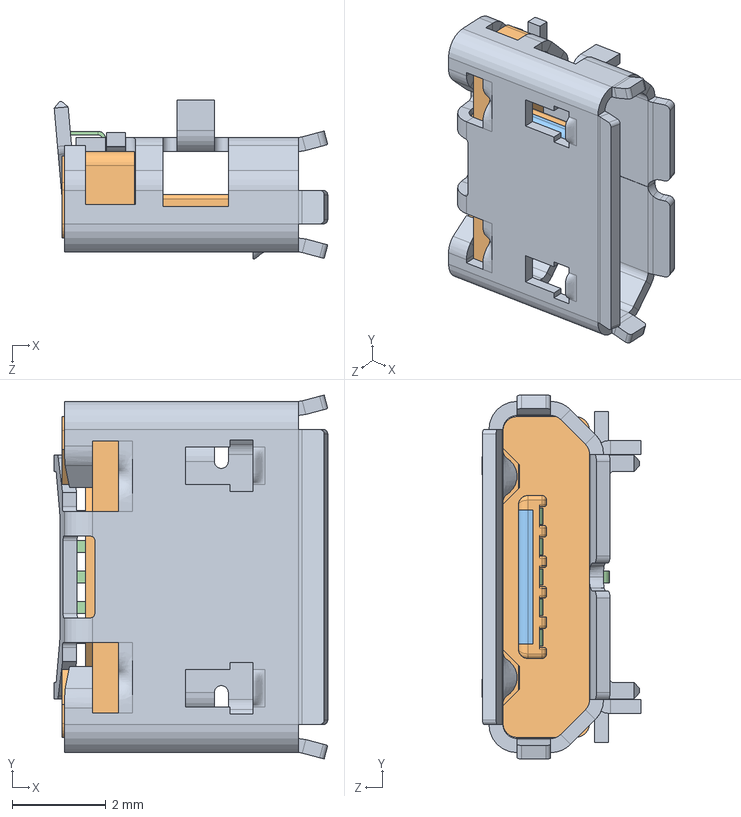
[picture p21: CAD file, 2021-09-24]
mech_design/CAD_model/micro_usb_connector.SLDASM
5.84 x 7.77 x 3.40 mm
shield.stp
socket_housing.stp
socket_plate.stp
terminal.stp x 5

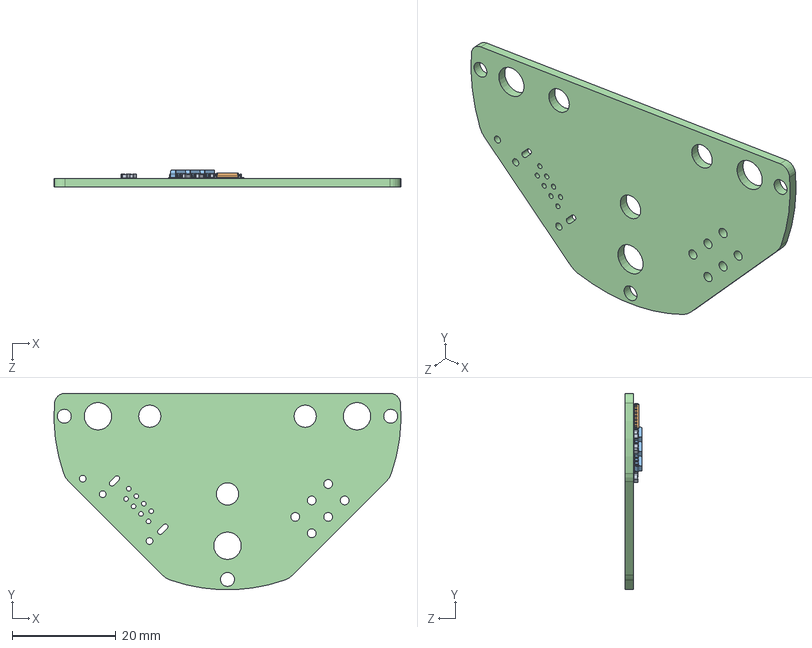
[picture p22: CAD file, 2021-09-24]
mech_design/CAD_model/motor-encoder-pcb.SLDASM
67.0 x 37.9 x 3.20 mm
SOLID-0.step x 9
SOLID-1.step
SOLID-2.step x 3
COMPOUND.step

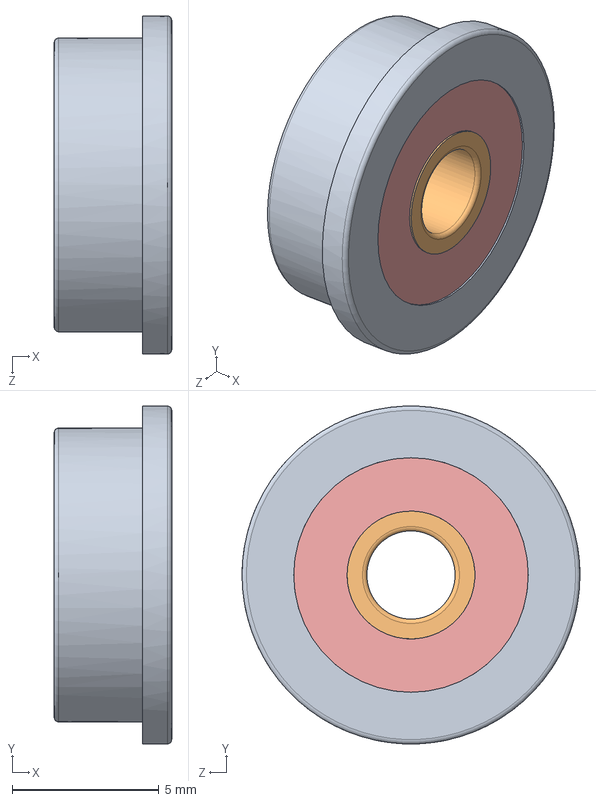
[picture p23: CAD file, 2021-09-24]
mech_design/CAD_model/F623ZZ v2.step.SLDASM
4.00 x 11.5 x 11.5 mm
F623ZZ Outer Ring.step
F623ZZ Inner Ring.step
F623ZZ Shield1.step
F623ZZ Ball.step x 7
F623ZZ Shield2.step

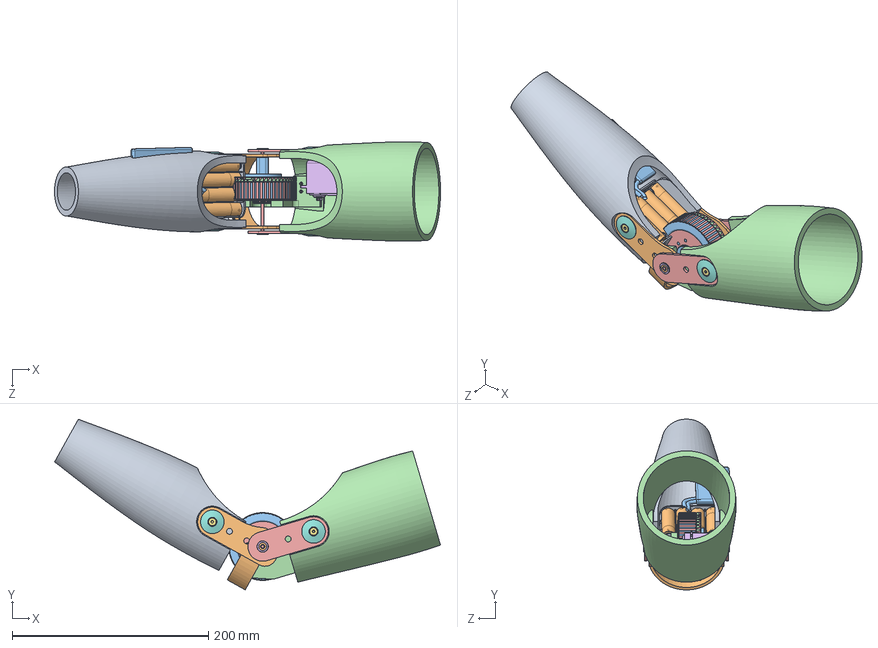
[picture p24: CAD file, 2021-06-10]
mech_design/CAD_model/lower_arm_assembly.SLDASM
392.9 x 173.9 x 101.2 mm
lower_arm_body
joint_lower
motor_front
motor_rear
Standard Servo
M4 x 10 csk machine screw x 4
flat_head_washer x 4
BatteryPack4AA
AABattery x 4
Battery
upper_arm_body
joint_upper x 2
F623ZZ Outer Ring.step x 2
F623ZZ Inner Ring.step x 2
F623ZZ Shield1.step x 2
F623ZZ Ball.step x 14
F623ZZ Shield2.step x 2
motor_adaptor
motor_bracket
main_axis

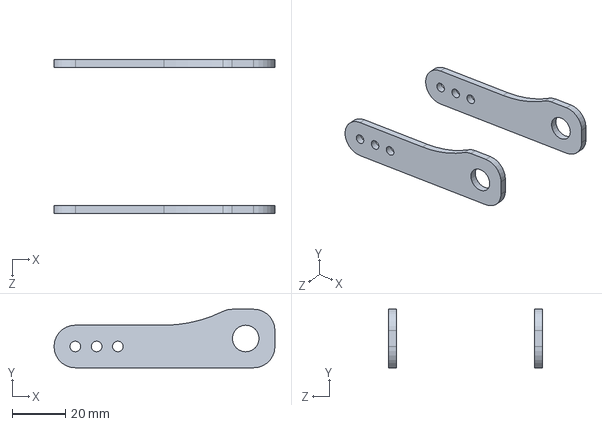
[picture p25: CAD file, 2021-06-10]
mech_design/CAD_model/joint_lower2_assy.SLDASM
83.0 x 22.0 x 57.9 mm
joint_lower2 x 2

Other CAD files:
mech_design/CAD_model/tssop-14_4.4x5mm_p0.65mm.step.SLDASM
mech_design/CAD_model/c_0603_1608metric.step.SLDASM
mech_design/CAD_model/sot-23-6.step.SLDASM
board_design/motor_encoder_pcb/motor_encoder_pcb.step
mech_design/CAD_DXF/motor_bracket_rotor_test.DXF
mech_design/CAD_DXF/motor_bracket_stator_test.DXF
mech_design/CAD_DXF/motor_bracket_stator_test2.DXF
mech_design/CAD_STL/encoder_spacer.STL
mech_design/CAD_STL/lower_arm_motor_adaptor_test.STL
mech_design/CAD_STL/magnet-bottom-bracket.STL
mech_design/CAD_STL/magnet-top-bracket.STL
mech_design/CAD_drawings/joint_lower.SLDDRW
mech_design/CAD_drawings/joint_lower_bridge.SLDDRW
mech_design/CAD_drawings/motor_bracket_rotor.SLDDRW
mech_design/CAD_drawings/motor_bracket_rotor_test.SLDDRW
mech_design/CAD_drawings/motor_bracket_stator.SLDDRW
mech_design/CAD_drawings/motor_bracket_stator_test.SLDDRW
mech_design/CAD_drawings/upper_plate.SLDDRW
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

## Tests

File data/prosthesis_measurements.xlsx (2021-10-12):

Prosthesis | Description |  | Mass (kg) | Length (m) | Moment on the elbow (Nm) |  | Weight measurement (kg) | Length of prosthesis (m) | Center of mass (m) | Tot mass of wooden plate (kg) | Mass of wooden plate on scale (m) | Tot length of wooden plate (m) | COM of wooden plate (m)
1 | Plastic demo prosthesis with no palm | No palm | 0.617 | 0.4 | 7.5254776 |  | 1.074 | 0.565 | 0.6636012966 | 1.186 | 0.571 | 0.814 | 0.3919005059
 |  | With black palm | 1.156 | 0.55
2 | Prosthesis with integrated palm 1 | No palm | 0.777 | 0.29 | 1.84461354 |  | 0.802 | 0.42 | 0.242 | 57.62% |  |  | m1L1/m2
 |  | With integrated palm |  | 0.42
3 | Prosthesis with integrated palm 2 | No palm | 0.609 | 0.29 | 1.58908266 |  | 0.77 | 0.46 | 0.2659868637 | 57.82%
 |  | With integrated palm |  | 0.46
4 | Prosthesis with integrated palm 3 | No palm | 0.768 | 0.31 | 1.86058422 |  | 0.804 | 0.44 | 0.2469557292 | 56.13%
 |  | With integrated palm |  | 0.44
5 | Prosthesis with integrated hook 1 | No hook | 0.704 | 0.22 | 0.79054866 |  | 0.67 | 0.36 | 0.11446875 | 31.80%
 |  | With integrated hook |  | 0.36
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

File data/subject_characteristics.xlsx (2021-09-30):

Subject ID | Age (yrs) | Height (cm) | Mass (kg) | Gender
id | 58 | 162 | 51 | m
jd | 57 | 176 | 79.5 | m
jr | 52 | 177 | 76 | m
ks | 55 | 164 | 59.3 | f
kw | 43 | 162 | 63.8 | f
lc | 50 | 158 | 61.2 | f
ld | 46 | 187.5 | 97.3 | m
ls | 57 | 163.5 | 82.2 | f
mk | 43 | 178 | 93.5 | m
mv | 55 | 180.5 | 98.5 | m
sm | 41 | 179 | 68.5 | m
td | 58 | 169 | 70 | m
tm | 46 | 173.5 | 66.2 | m
AVERAGE | 50.84615385 | 171.5 | 74.4
SD | 6.335694567 | 9.0 | 15.1

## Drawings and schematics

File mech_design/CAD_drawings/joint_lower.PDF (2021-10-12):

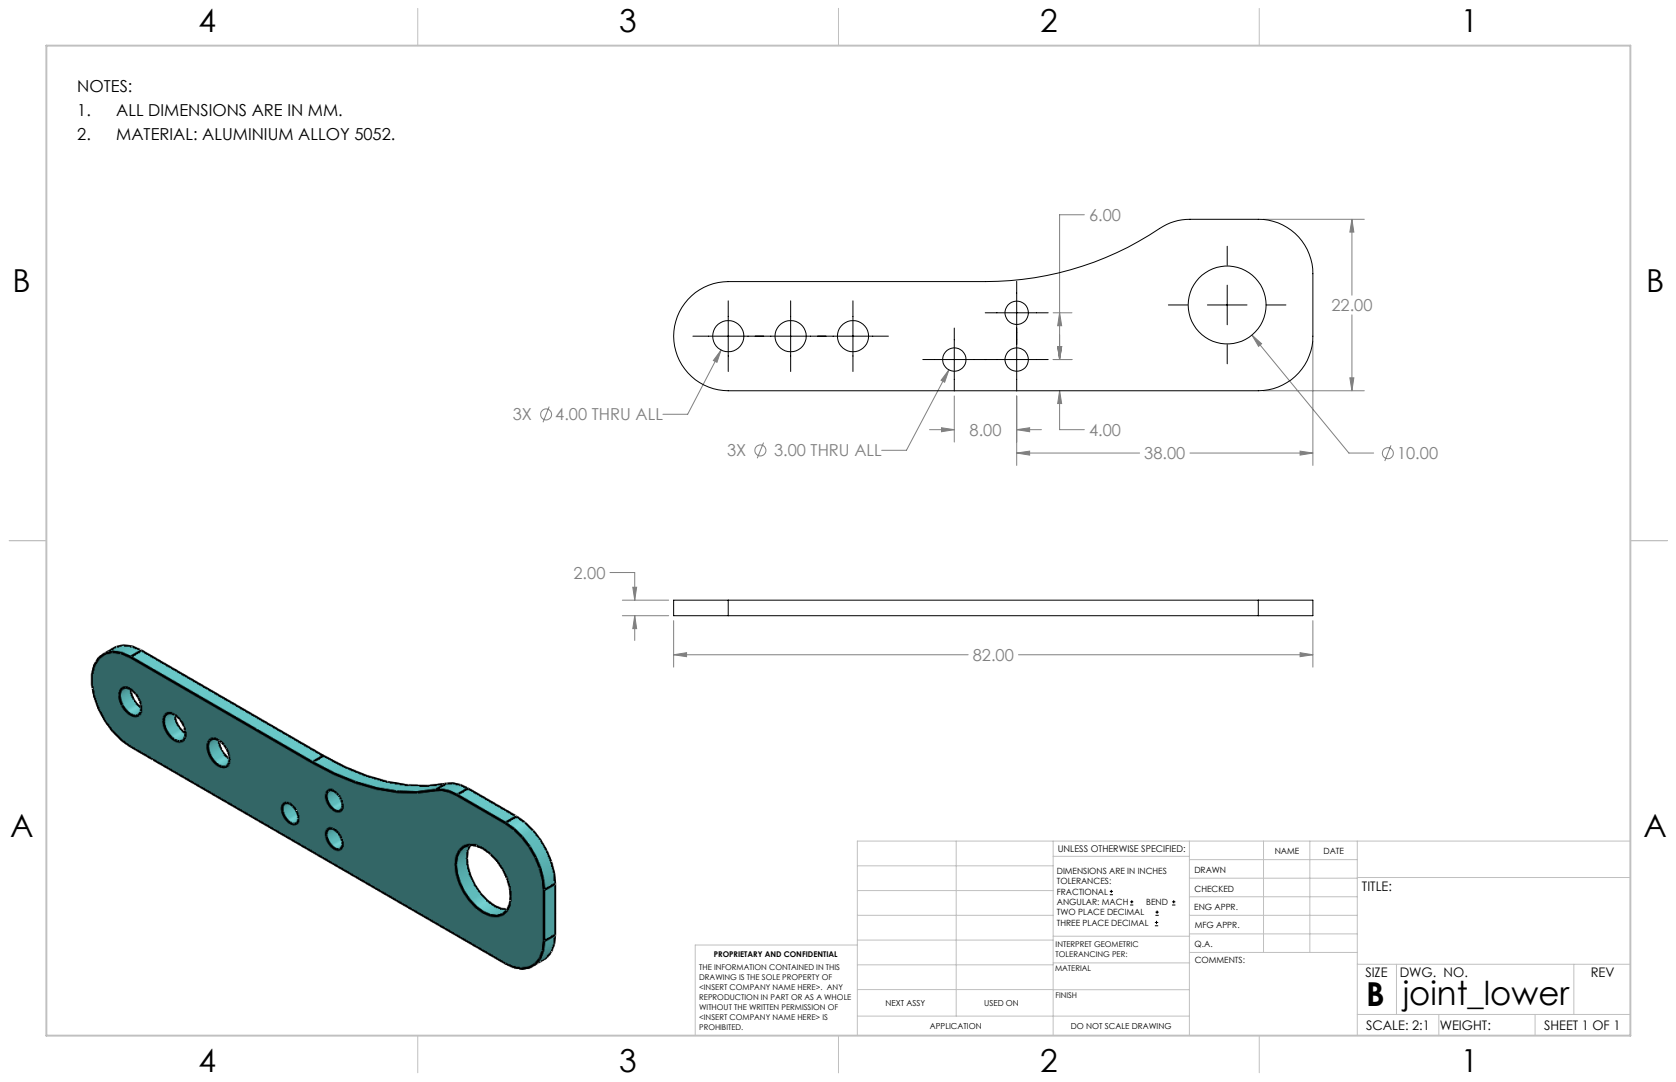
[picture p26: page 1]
3X 4.00 THRU ALL; 3.00 THRU ALL

NOTES:
1. ALL DIMENSIONS ARE IN MM.
2. MATERIAL: ALUMINIUM ALLOY 5052.

UNLESS OTHERWISE SPECIFIED: | | NAME | DATE
DIMENSIONS ARE IN INCHES TOLERANCES: FRACTIONAL ANGULAR: MACH BEND TWO PLACE DECIMAL THREE PLACE DECIMAL | DRAWN

CHECKED | | | TITLE:

ENG APPR.
MFG APPR.

INTERPRET GEOMETRIC TOLERANCING PER: | Q.A.
MATERIAL | | SIZE B | DWG. NO. joint_lower | REV

PROPRIETARY AND CONFIDENTIAL
THE INFORMATION CONTAINED IN THIS
DRAWING IS THE SOLE PROPERTY OF
<INSERT COMPANY NAME HERE>. ANY
REPRODUCTION IN PART OR AS A WHOLE
WITHOUT THE WRITTEN PERMISSION OF
<INSERT COMPANY NAME HERE> IS
PROHIBITED.

NEXT ASSY | USED ON | FINISH

APPLICATION | DO NOT SCALE DRAWING | | SCALE: 2:1 | WEIGHT: | SHEET 1 OF 1

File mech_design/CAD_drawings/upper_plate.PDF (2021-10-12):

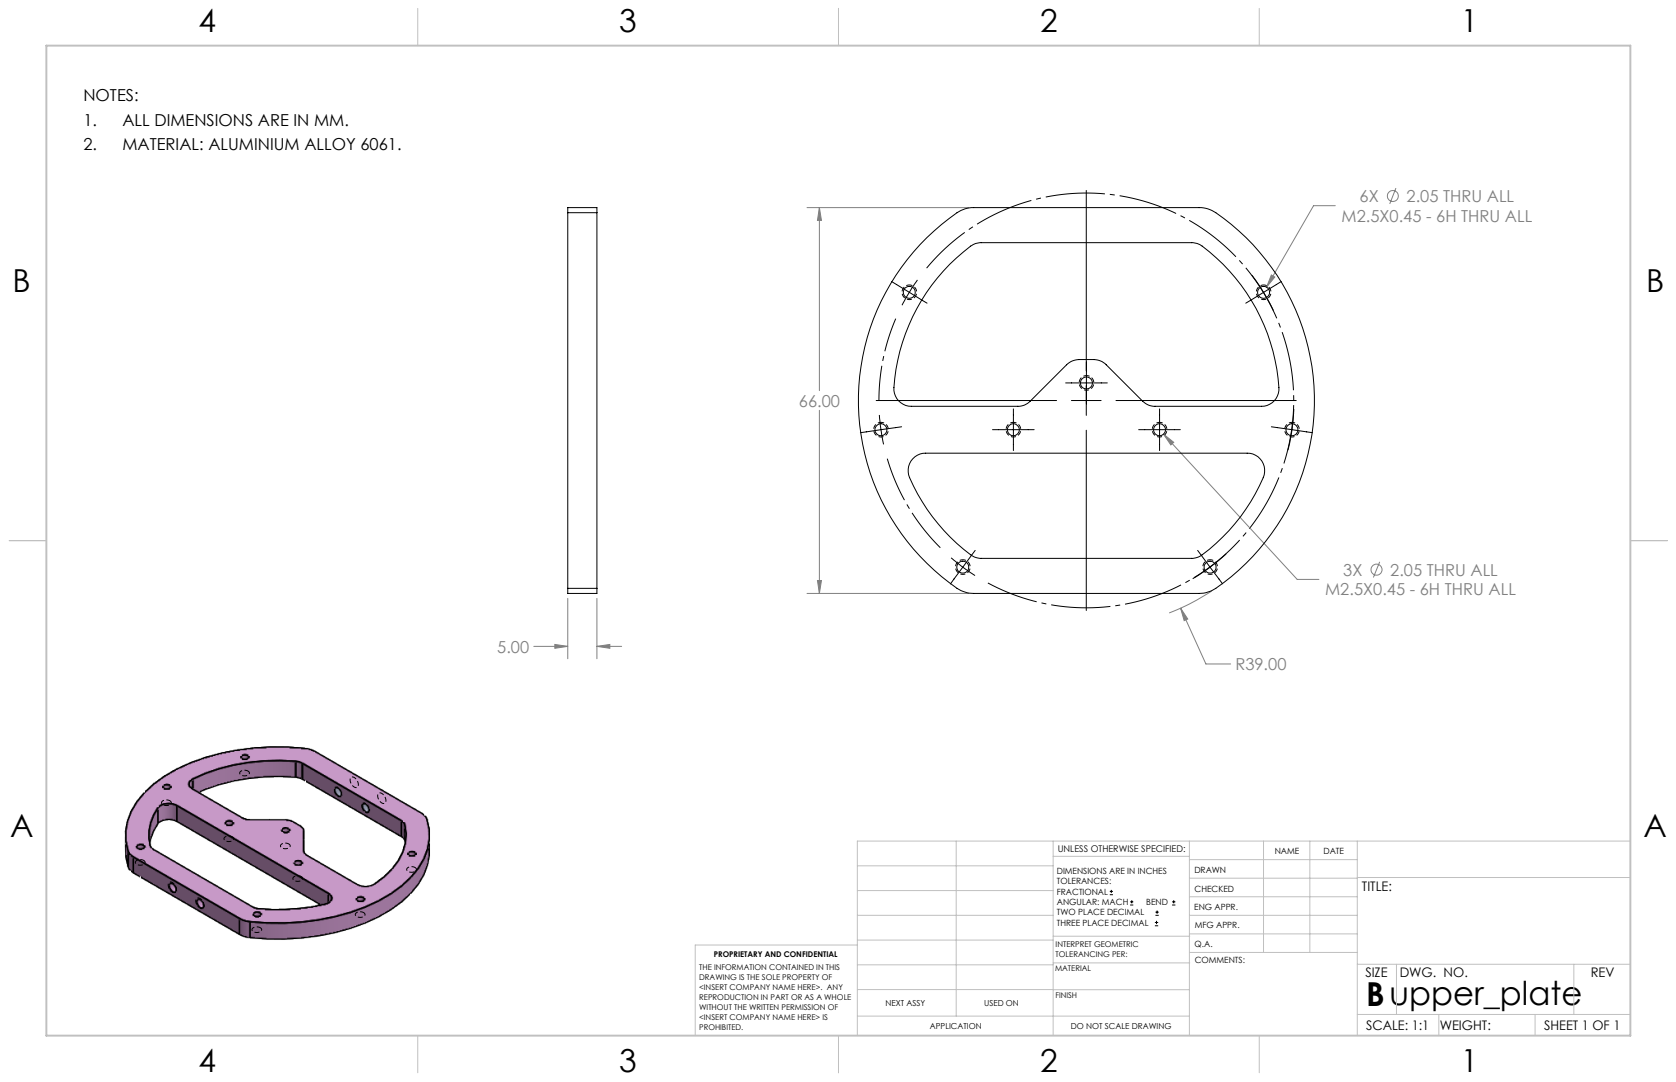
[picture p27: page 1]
2.05 THRU ALL; M2.5X0.45 - 6H THRU ALL

NOTES:
1. ALL DIMENSIONS ARE IN MM.
2. MATERIAL: ALUMINIUM ALLOY 6061.

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

CHECKED | | | TITLE:

ENG APPR.
MFG APPR.

INTERPRET GEOMETRIC TOLERANCING PER: | Q.A.
MATERIAL | | SIZE B upper_plate | DWG. NO. | REV

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

NEXT ASSY | USED ON | FINISH

APPLICATION | DO NOT SCALE DRAWING | | SCALE: 1:1 | WEIGHT: | SHEET 1 OF 1

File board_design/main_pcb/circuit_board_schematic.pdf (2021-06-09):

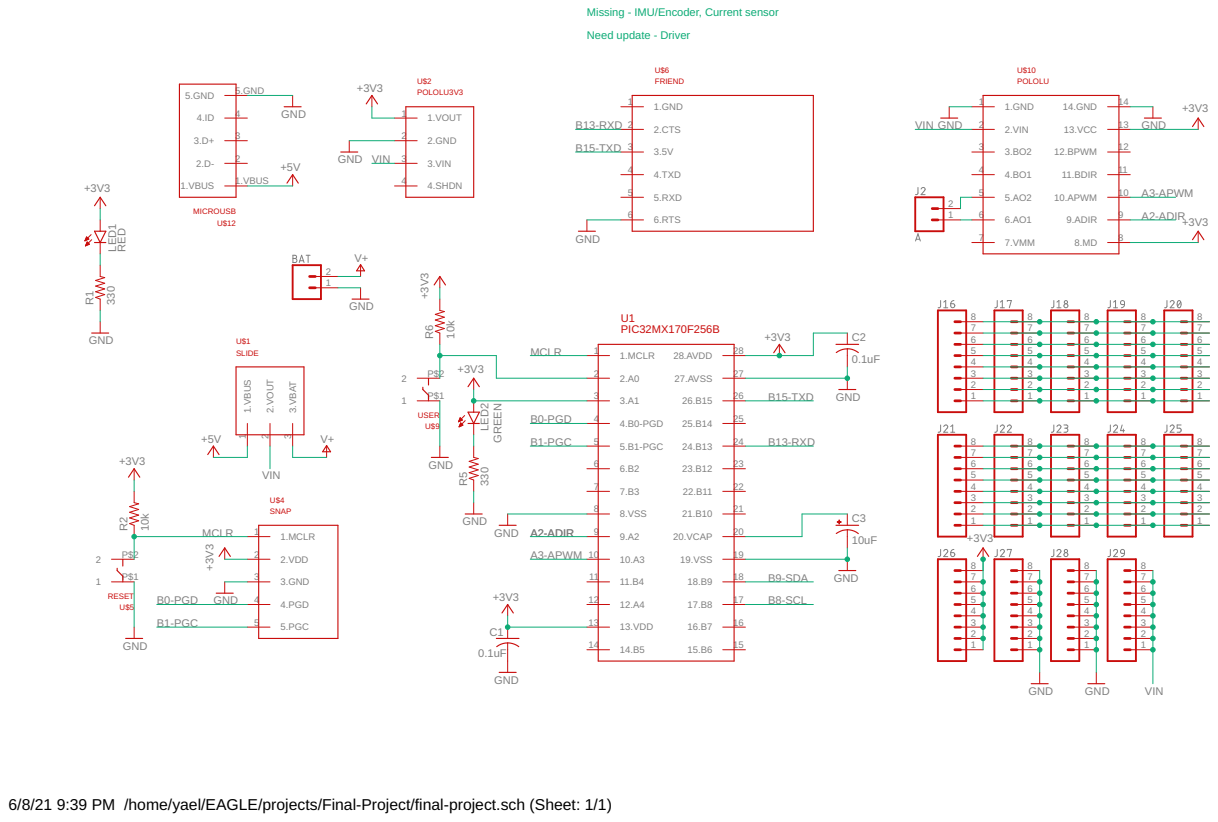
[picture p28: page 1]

Need update - Driver Missing - IMU/Encoder, Current sensor

6/8/21 9:39 PM /home/yael/EAGLE/projects/Final-Project/final-project.sch (Sheet: 1/1)

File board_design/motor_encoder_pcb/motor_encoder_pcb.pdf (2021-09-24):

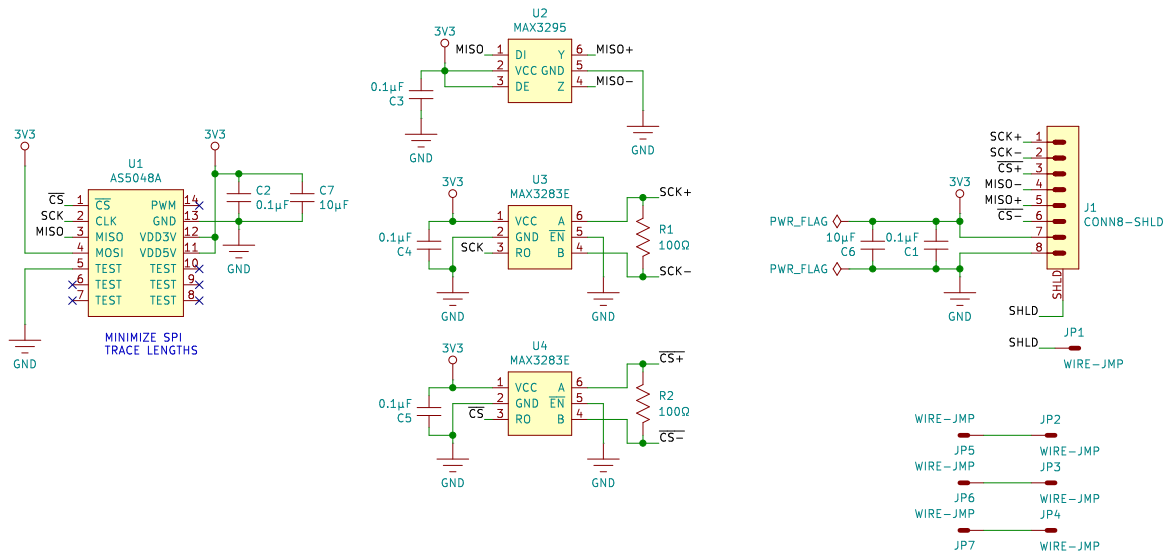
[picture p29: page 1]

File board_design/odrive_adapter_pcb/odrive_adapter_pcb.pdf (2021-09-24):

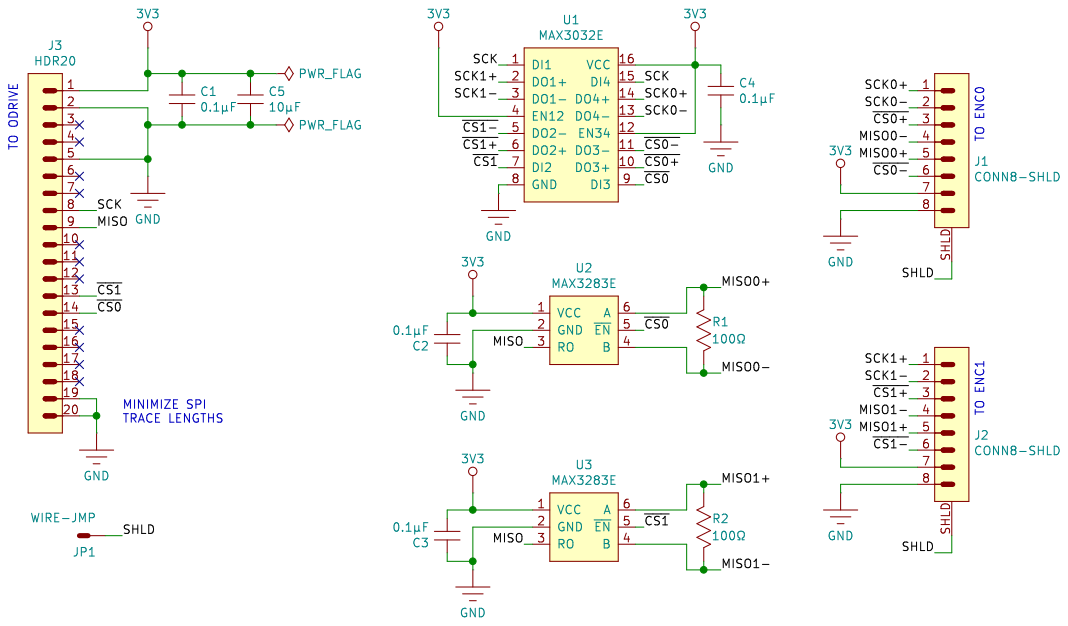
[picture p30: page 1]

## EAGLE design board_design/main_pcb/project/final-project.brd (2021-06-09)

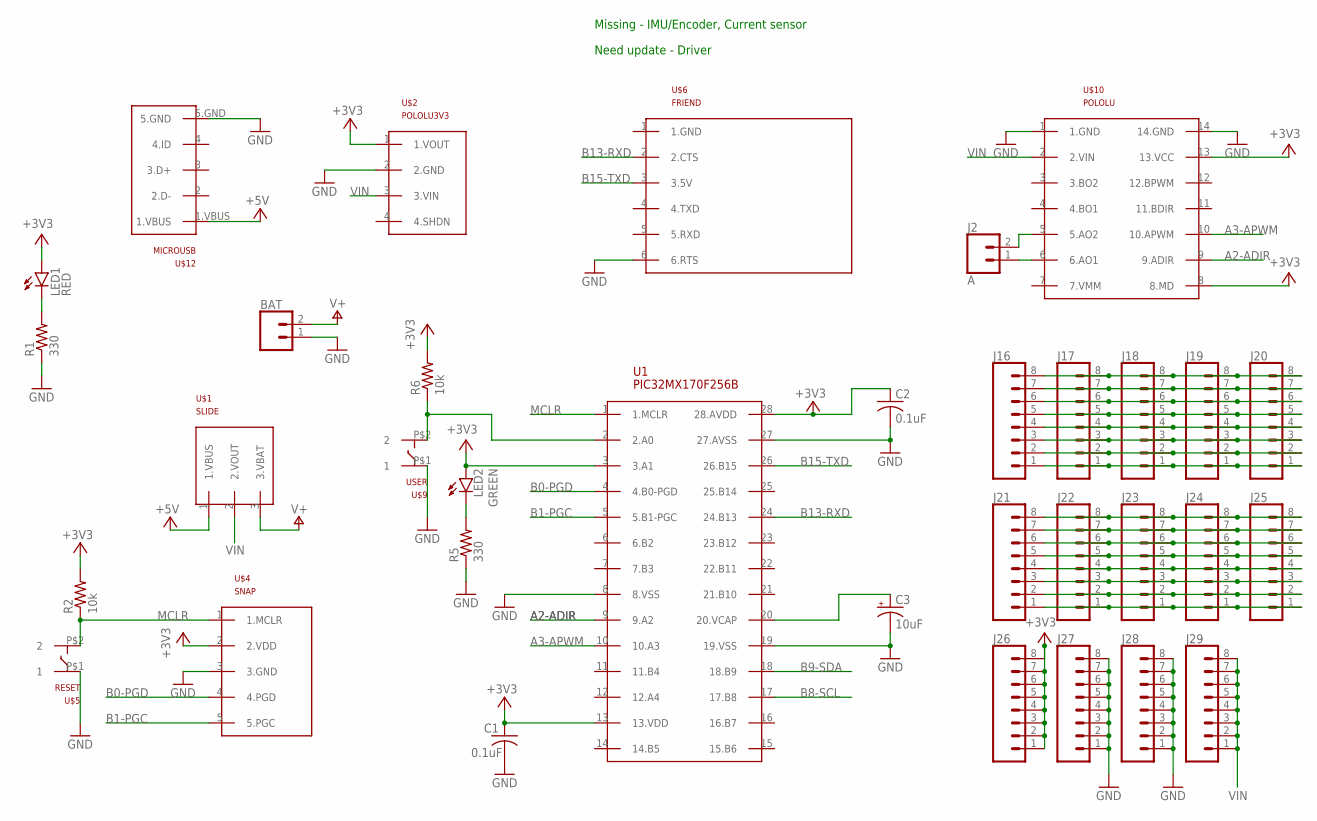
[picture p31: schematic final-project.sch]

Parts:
BAT: CONN_02; 1X02
C1, C2: 0.1uF; C025-030X050
C3: 10uF; B45181B
J2: A; 1X02
J16, J17, J18, J19, J20, J21, J22, J23, J24, J25, J26, J27, J28, J29: CONN_08"; 1X08
LED1: RED; LED3MM
LED2: GREEN; LED3MM
R1, R5: 330; 0207/10
R2, R6: 10k; 0207/10
U1: PIC32MX170F256B; DIL28-3
U$1: SLIDE
U$2: POLOLU3V3
U$4: SNAP
U$5: RESET; PUSH
U$6: FRIEND
U$9: USER; PUSH
U$10: POLOLU
U$12: MICROUSB

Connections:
+3V3: C1.1, C2.1, J26.1, J26.2, J26.3, J26.4, J26.5, J26.6, J26.7, J26.8, LED1.A, LED2.A, R2.2, R6.2, U1.3 (3.A1), U1.13 (13.VDD), U1.28 (28.AVDD), U$2.1 (1.VOUT), U$4.2 (2.VDD), U$10.8 (8.MD), U$10.13 (13.VCC)
+5V: U$1.1 (1.VBUS), U$12.1.VBUS
A2-ADIR: U1.9 (9.A2), U$10.9 (9.ADIR)
A3-APWM: U1.10 (10.A3), U$10.10 (10.APWM)
B0-PGD: U1.4 (4.B0-PGD), U$4.4 (4.PGD)
B1-PGC: U1.5 (5.B1-PGC), U$4.5 (5.PGC)
B8-SCL: U1.17 (17.B8)
B9-SDA: U1.18 (18.B9)
B13-RXD: U1.24 (24.B13), U$6.2 (2.CTS)
B15-TXD: U1.26 (26.B15), U$6.3 (3.5V)
GND: BAT.1, C1.2, C2.2, C3.-, J27.1, J27.2, J27.3, J27.4, J27.5, J27.6, J27.7, J27.8, J28.1, J28.2, J28.3, J28.4, J28.5, J28.6, J28.7, J28.8, R1.1, R5.1, U1.8 (8.VSS), U1.19 (19.VSS), U1.27 (27.AVSS), U$2.2 (2.GND), U$4.3 (3.GND), U$5.P$1 (1), U$6.6 (6.RTS), U$9.P$1 (1), U$10.1 (1.GND), U$10.14 (14.GND), U$12.5.GND
MCLR: R2.1, U1.1 (1.MCLR), U$4.1 (1.MCLR), U$5.P$2 (2)
MCLR1: R6.1, U1.2 (2.A0), U$9.P$2 (2)
unnamed: LED1.K (C), R1.2
unnamed: C3.+, U1.20 (20.VCAP)
unnamed: LED2.K (C), R5.2
unnamed: J2.1, U$10.6 (6.AO1)
unnamed: J2.2, U$10.5 (5.AO2)
unnamed: J16.8, J17.8, J18.8, J19.8, J20.8
unnamed: J16.7, J17.7, J18.7, J19.7, J20.7
unnamed: J16.6, J17.6, J18.6, J19.6, J20.6
unnamed: J16.5, J17.5, J18.5, J19.5, J20.5
unnamed: J16.4, J17.4, J18.4, J19.4, J20.4
unnamed: J16.3, J17.3, J18.3, J19.3, J20.3
unnamed: J16.2, J17.2, J18.2, J19.2, J20.2
unnamed: J16.1, J17.1, J18.1, J19.1, J20.1
unnamed: J21.8, J22.8, J23.8, J24.8, J25.8
unnamed: J21.7, J22.7, J23.7, J24.7, J25.7
unnamed: J21.6, J22.6, J23.6, J24.6, J25.6
unnamed: J21.5, J22.5, J23.5, J24.5, J25.5
unnamed: J21.4, J22.4, J23.4, J24.4, J25.4
unnamed: J21.3, J22.3, J23.3, J24.3, J25.3
unnamed: J21.2, J22.2, J23.2, J24.2, J25.2
unnamed: J21.1, J22.1, J23.1, J24.1, J25.1
V+: BAT.2, U$1.3 (3.VBAT)
VIN: J29.1, J29.2, J29.3, J29.4, J29.5, J29.6, J29.7, J29.8, U$1.2 (2.VOUT), U$2.3 (3.VIN), U$10.2 (2.VIN)

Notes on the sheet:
Need update - Driver
Missing - IMU/Encoder, Current sensor

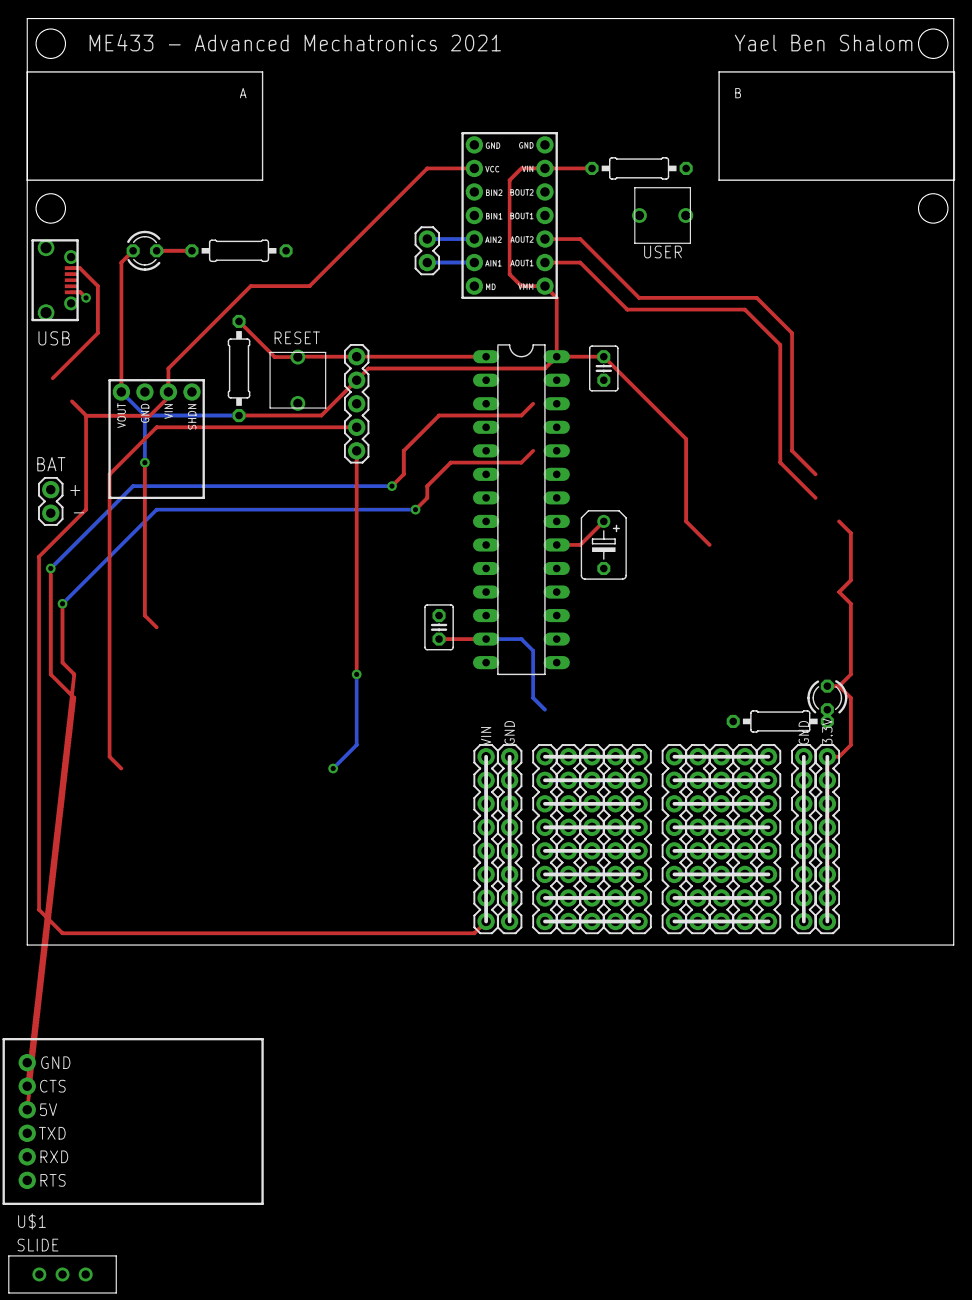
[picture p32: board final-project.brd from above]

Board: 2 copper layers, 100.0 x 100.0 mm, 34 parts (0 on the bottom side), 34 nets.

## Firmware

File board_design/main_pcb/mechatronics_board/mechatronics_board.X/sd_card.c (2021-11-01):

#include "sd_card.h"

/*   send a command to the SD card   */
int SDcmd(unsigned char comd, unsigned int a, unsigned char crc)
{
  /*
   comd   command code
   a      data block address
   */
  int i, r;

  // send 6-byte command packet
  spi_io(comd | 0x40); // send command
  spi_io(a >> 24);     // address MSB
  spi_io(a >> 16);
  spi_io(a >> 8);
  spi_io(a);          // address LSB
  spi_io(crc | 0x01); // CRC

  // send up to 8 bytes while waiting for response
  for (i = 0; i < 8; i++)
  {
    r = spi_io(0xFF);
    if (r != 0xFF)
    {
      break;
    }
  }

  return r;
}

int initSD()
{
  /*

   */
  int i, r;
  int res[5];
  char message[50];

  SPI1BRG =
      95; // set SPI baud rate to 250kHz until SD card properly initialized

  // allow 80 clock cycles for startup
  for (i = 0; i < 10; i++)
  {
    spi_io(0xFF);
  }

  // reset the SD card
  SD_CS = 0;
  r = SDcmd(CMD0, CMD0_ARG, CMD0_CRC); // GO_IDLE_STATE
  SD_CS = 1;
  if (r != 1)
  { // return command error if IDLE not returned
    return COMD_ERR;
  }

  // send interface condition
  SD_CS = 0;
  res[0] = SDcmd(CMD8, CMD8_ARG, CMD8_CRC); // SEND_IF_COND

  // R1 byte of R7 response must equal 0x00 or 0x01
  if (res[0] > 1)
  {
    return res[0];
  }

  // read remaining four bytes of R7 response
  for (i = 1; i < 5; i++)
  {
    res[i] = spi_io(0xFF);
  }
  SD_CS = 1;

  // send operating condition
  SD_CS = 0;
  for (i = 0; i < 10000; i++)
  {
    SDcmd(CMD55, CMD55_ARG, CMD55_CRC);        // application command notifier
    r = SDcmd(ACMD41, ACMD41_ARG, ACMD41_CRC); // operating condition command
    if (!r)
    { // break loop once IDLE ends (command response = 0)
      SD_CS = 1;
      break;
    }
  }
  if (i == 10000)
  {
    return TIMEOUT_ERR; // return timeout error if IDLE does not terminate
  }

  // return SPI communication rate to maximum
  SPI1CON = 0;      // disable SPI1
  SPI1BRG = 1;      // set baud rate to 12 MHz
  SPI1CON = 0x8120; // re-enable SPI1

  return r;
}

int SDwrite(unsigned int addr, char *p, unsigned char *token)
{
  /*
   Write a 512-byte-wide block of data to the SD card

   addr       32-bit logic block address
   p          pointer to data buffer
   token      pointer to response token
   */
  int i, r, read;
  char message[50];

  *token = 0xFF;

  // set CS pin low
  SD_CS = 0;

  // WRITE_BLOCK
  r = SDcmd(CMD24, addr, CMD24_CRC);

  if (r == 0)
  { // check if command was accepted
    // send data start token
    spi_io(DAT_START);

    // write buffer to card
    for (i = 0; i < SD_BLOCKLEN; i++)
    {
      spi_io(p[i]);
    }
    // send 16-bit dummy CRC
    spi_io(0xFF);
    spi_io(0xFF);

    // wait for a response, 250ms timeout
    TMR4 = 0;
    while (TMR4 < 46874)
    {
      if ((read = spi_io(0xFF)) != 0xFF)
      {
        *token = 0xFF;
        break;
      }
    }

    // check if data accepted
    if ((read & 0x1F) == DAT_ACC)
    {
      *token = DAT_ACC; // set token to data accepted

      // wait for write completion, 250ms timeout
      TMR4 = 0;
      while (spi_io(0xFF) == 0x00)
      {
        if (TMR4 > 46874)
        {                // if timeout reached
          *token = 0x00; // set token to write complete timeout
          break;
        }
      }
    }
  }

  SD_CS = 1; // set CS pin high

  return r; // returns 0 if command accepted,
            // combine with token to know if write successful
}

int SDread(unsigned int addr, char *p, unsigned char *token)
{
  /*
   Read a 512-byte-wide block of data from the SD card
   */
  int i, r, read;

  *token = 0xFF;

  SD_CS = 0; // set CS pin low

  r = SDcmd(CMD17, addr, CMD17_CRC); // READ_BLOCK

  // if the card sends a response
  if (r != 0xFF)
  {
    // wait for a response token
    TMR4 = 0;
    while (TMR4 < 18749)
    {
      if ((read = spi_io(0xFF)) != 0xFF)
      {
        break;
      }
    }

    // if response token is received
    if (read == 0xFE)
    {
      // read 512-byte block
      for (i = 0; i < SD_BLOCKLEN; i++)
      {
        p[i] = spi_io(0xFF);
      }

      // read 16-bit CRC
      spi_io(0xFF);
      spi_io(0xFF);
    }

    // set token to card response
    *token = read;
  }

  SD_CS = 1; // set CS pin high

  return r; // returns card response to CMD17,
            // combine with token to know if read successful
}

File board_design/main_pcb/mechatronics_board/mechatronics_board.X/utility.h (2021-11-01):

#ifndef UTIL__H__
#define UTIL__H__

#include <stdio.h> // standard input/output
#include <xc.h>

// pin definitions
#define SD_CS_TRIS TRISAbits.TRISA0 // sd card chip select
#define SD_CS LATAbits.LATA0
#define CD_TRIS TRISAbits.TRISA1 // sd card detect
#define CD PORTAbits.RA1
#define ERR_LED_TRIS TRISBbits.TRISB4 // indicator LED
#define ERR_LED LATBbits.LATB4
#define HB_LED_TRIS TRISBbits.TRISB5 // heartbeat LED
#define HB_LED LATBbits.LATB5
#define USR_TRIS TRISBbits.TRISB6 // USER button
#define USR PORTBbits.RB6
#define IMU_CS_TRIS TRISBbits.TRISB15 // IMU chip select
#define IMU_CS LATBbits.LATB15

// constants
extern const double TICK;
extern const double GRAV;
extern double ACQ_FREQ;

extern int t_LED;

int debounce_user();
void heartbeat();
void initTimers();
void shift_vector(double *vector, int size);
double max_double(double *vector, int size);

#endif

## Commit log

2021-05-17 add the data and jupyter notebook
    [ID_WS1.XLS, ID_WS2.XLS, ID_WS3.XLS, ID_WS4.XLS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]
2021-05-24 add data-reading script and update jupyter notebook
    [ID_WS1.csv, ID_WS2.csv, ID_WS3.csv, ID_WS4.csv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]
2021-06-03 add mech design repo
    [4x AA Alkaline 1.5 V Battery Pack.x_t, F623ZZ v2.step, Flat Washer ISO 7089.SLDPRT, M4 x 10 csk machine screw.SLDPRT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]
2021-06-09 add board design files
    [4x AA Alkaline 1.5 V Battery Pack.x_t, DIN 7991.SLDPRT, EC60fl-200W-V1.stp, EC60fl-200W-V2.stp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]
2021-06-10 add mech design
    [10x_Male_Pin_2.54_mm.STEP, 1x_Male_Pin_2.54_mm.STEP, 2x_Male_Pin_2.54_mm.STEP, 3x_Male_Pin_2.54_mm.STEP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]
2021-06-10 add board lobraries
    [final-project.brd, final-project.sch]
2021-09-24 update mech design
    [1734795-1.step.SLDASM, 1_Male_Pin_2.54_mm.STEP.SLDPRT, 4x AA Alkaline 1.5 V Battery Pack.SLDASM, 4x AA Alkaline 1.5 V Battery Pack.x_t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]
2021-09-29 add ODrive submodule
    [encoder_spacer.STL, magnet-bottom-bracket.STL, magnet-top-bracket.STL]
2021-09-30 add calculations
    [Motor Selection.xlsx, Prosthesis Measurements.xlsx, Subject Characteristics.xlsx, System BOM.xlsx]
2021-10-04 update motor_control script
2021-10-04 update file names
    [ID_WS1.XLS, ID_WS1.csv, ID_WS2.XLS, ID_WS2.csv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]
2021-10-04 add mechatronics board
2021-10-04 update jupyter notebook
    [subject_characteristics.xlsx, subjectcharacteristics.xlsx]
2021-10-04 update data scripts
    [system_BOM.xlsx]
2021-10-06 update model & control
    [10x_Male_Pin_2.54_mm.STEP, 1734795-1.step.SLDASM, 1_Male_Pin_2.54_mm.STEP.SLDPRT, 1x_Male_Pin_2.54_mm.STEP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]
2021-10-06 add a test bracket dxf
    [motor_bracket_stator_test2.DXF]
2021-10-11 add motor_control branch
2021-10-12 update test files
    [lower_arm_motor_adaptor_test.STL, prosthesis_measurements.xlsx]
2021-10-12 add calibration
2021-10-12 add walking data
    [Subject Key.xlsx]
2021-10-15 add hand-back motion data
    [Subject Key.xlsx]
2021-10-15 add txt to csv converter
    [MT_012006A8-2021-10-15-10h51_000-0-000_00B429E2_0.5ms.csv, MT_012006A8-2021-10-15-10h51_000-0-000_00B429F8_0.5ms.csv, MT_012006A8-2021-10-15-10h51_000-0-000_00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]
2021-10-19 update data
    [MT_012006A8-2021-10-15-10h51_000-0-000_00B429E2_0.5ms.csv, MT_012006A8-2021-10-15-10h51_000-0-000_00B429F8_0.5ms.csv, MT_012006A8-2021-10-15-10h51_000-0-000_00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]
2021-10-20 update data processing
    [ID_WS3.csv, MT_012006A8-2021-10-15-11h53_000-1-000_00B429F8_1.0ms.csv]
2021-10-22 update CAD model
    [encoder_spacer.STL, lower_arm_motor_adaptor_test.SLDPRT, lower_arm_motor_adaptor_test.STL, magnet-bottom-bracket.STL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]
2021-10-28 remove image
    [motor_selection.xlsx]
2021-11-01 add motor selection to jupyter notebook
2021-11-02 tune motor
2021-11-11 tune controller
    [PID_tune.xlsx]
2021-11-23 add data script
    [05ms.csv, 06ms.csv, 07ms.csv, 08ms.csv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]
2021-11-30 update motorized prosthetic project
2021-12-09 remove unused data
    [Subject Key.xlsx]
